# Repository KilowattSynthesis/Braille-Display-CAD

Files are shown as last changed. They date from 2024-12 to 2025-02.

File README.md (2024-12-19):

# Braille-Display-CAD

Experimental design for a braille display using build123d CAD in Python

## Interesting Parts

* 4mm x 8mm DC Motors: https://www.aliexpress.com/item/1005004370822475.html
* 2.8mm x 3.9mm DC Motors: https://www.aliexpress.com/item/1005006897190118.html

## Explored Ideas

### Pogo Spools

* Laser printer fuser-like roller mask.
    * Branch: `archive/pogo-spools`
    * Files: `ideas_pogo_spool_mask/`
* Made PCB with small stepper motors, tiny CAD parts (spools).

### RF Inductors as Electromagnets

* Use Mouser's "RF Inductors" selection, mounting an inductor vertically.
    * Branches: `archive/inductor-smd-vertical`, `archive/inductor-smd-flat`
    * Eaton makes good-looking ones. 3225 metric (1210 imp) is too big; 2520 metric (1008 imp) might be okay. 2012 metric (0805 imp) is great!
    * "Power Inductors - Leaded" are never small enough.
    * Filter to >= 20uH inductance. Filter to >=70 mA.
    * Examples (Vertical-Mount):
        * BWLD00241715 -> Not stocked in smaller quantities, though.
            * 2.4 mm x 1.72 mm x 1.52 mm
        * LBR2012T470M -> 0805 imp (2012 metric). 47uH. 75mA rated max.
    * Examples (Horizontal-Mount):
        * VLS201612CX-220M-1 -> 22uF, very good, but shielded.

* Test results:
    * 4mm x 4mm x 3mm 33uH coil-wound SMD power inductor (ASPI-4030S-330M-T) can point a magnet. Magnets stick to the inductor always though.
    * Several inductors, up to 6mm diameter (and 1-2 MH), with 24V get very hot, but don't levitate a 1mm or 2mm neodymium magnet.
        * Good at pointing pointing the magnet, if it starts far away.
        * Cannot remove the magnet from the inductor once it's stuck.

* **Conclusion**: RF inductors don't have enough magnetic force to levitate 1mm or 2mm neodymium magnets.

### Nut/Bolt Grid

* Turn a bolt in a threaded hole/nut. Each bolt is a dot. User directly touches the dot.
* Movement can be done with one motor per dot (very tiny motors, maybe stacked), or motors can be moved between dots (CNC plotter style). Multiple heads can be used.
* Branch: `archive/cnc-plotter`
* Files: `cad/nut_bolt_grid.py`, `cad/vertical_motor_layers.py`

### Silicone Sheet

* Use CNC plotter to manipulate a silicone sheet which can pop up and down.
    * Branch: `archive/silicone-sheet`
    * Files: `cad/silicone_sheet_mold/`

## Unexplored/Unrealized Ideas

* Investigate bi-metallic strip with actuator.
* Investigate shape memory alloy (SMA) approach. Benefit: Would be very quiet.
* Should buy some 4mm solenoids.

* Key and lock mechanism pushes up on the pins

* Use GT2 belt (or similar) to press up on pins.
    * T2.5 belt is probably best - https://www.aliexpress.com/item/1005004668423141.html
    * Could try to TPU 3D print belt with the perfect braille pattern, in a closed loop. Teeth on the inside, and pattern on the outside.
    * Spring pushing on pogo pin flange, on solenoid-relieved cell frame.

* Use CNC plotter to turn pins/bolts for placement. Use hex drive, plus solenoid to mate/un-mate. Build the plotter on a PCB with 3mm linear rails, belts, etc.
    * Branch: `cnc-plotter`
    * Bolt options - Search "M2.5 plunger"
    * Best option: M1.6 Grub Screw, probably.
    * Create top plate with Z-stacked nuts on it.
    * Screw driver or nut will move up and down and turn screws.
    * Search "Micro Linear Motor" for gantry.
    * Focus on M1.6 and M2.5 designs.
    * To move the screw:
        * Use a spring to push the bit up, and a solenoid to pull it down.
        * Use a hex bit maybe, or use rubber friction.
    * BOM:
        * LM3UU linear bearings (ID=3mm, OD=7mm, L=10mm)
        * 3mm Rod x 100mm
        * PM15S Stepper Motors: https://www.aliexpress.com/item/1005005152436475.html
        * GT2 belt
        * GT2 pulley, custom to mate with stepper motor's gear.

* Motors mounted on orthogonal PCBs, with rotating slanted plate to push on the pins.
    * Use magnets as the mating, somehow.

* Microfluidics as valves.

* MEMS on-chip stepper motor:
    * https://www.youtube.com/watch?v=n3YMjgbhvTA
    * Could be useful to drive the screws on the CNC Plotter style.

* Double screw with balls and weird geometry.

* Cams on 2.4mm diameter rods that run along each column of dots.
    * Each cam would have 8 positions, so 45 degrees per position.
    * Would probably need to move table up-and-down independently of the cams.
    * One motor per cam, probably.

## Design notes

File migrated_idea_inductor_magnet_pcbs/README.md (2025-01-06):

This idea (`idea_inductor_magnet_pcbs`) has been moved to this repo: https://github.com/KilowattSynthesis/Braille-Display-Inductors-CAD

Rev 1 PCBs are present here. Rev 2 (another attempt at tiny inductors), and Rev 3 (using 2x big inductors per cell) are in the linked repo.

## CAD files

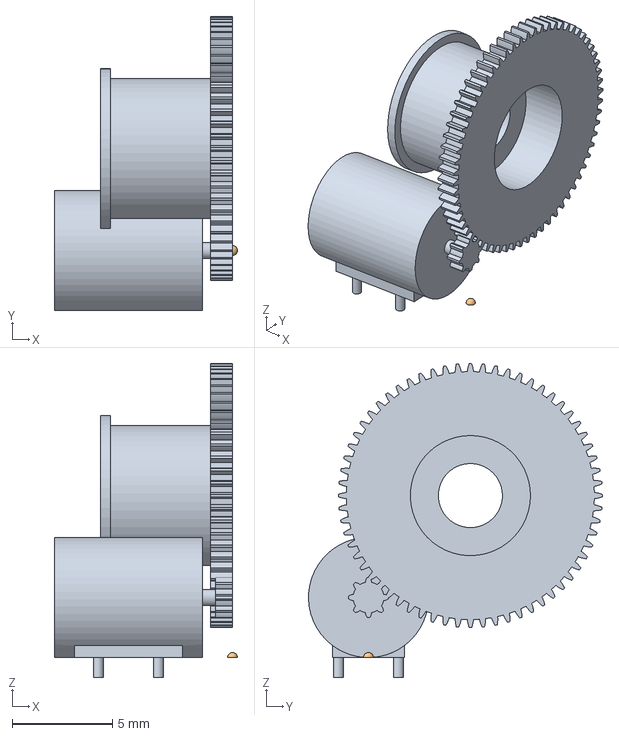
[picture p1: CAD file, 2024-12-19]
idea_pogo_spool_mask/pcb/Braille-Pogo-Frame/lib-cad/spool_motor_assembly.step
9.15 x 14.7 x 15.7 mm

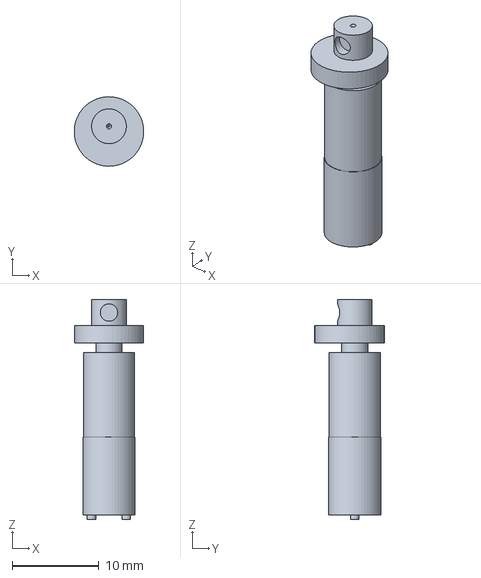
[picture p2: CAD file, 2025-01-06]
migrated_idea_column_rods/Braille-Column-Rods-PCB/lib-cad/assembly_cam_and_dc_motor.step
7.99 x 8.00 x 25.3 mm

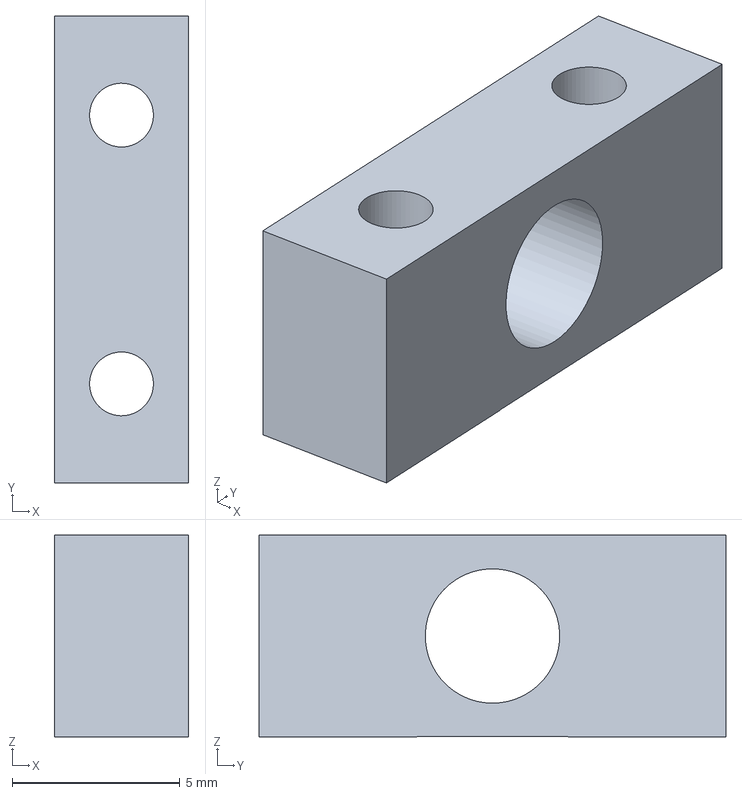
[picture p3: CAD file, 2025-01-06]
migrated_idea_column_rods/Braille-Column-Rods-PCB/lib-cad/bushing_block.step
4.00 x 13.9 x 6.00 mm

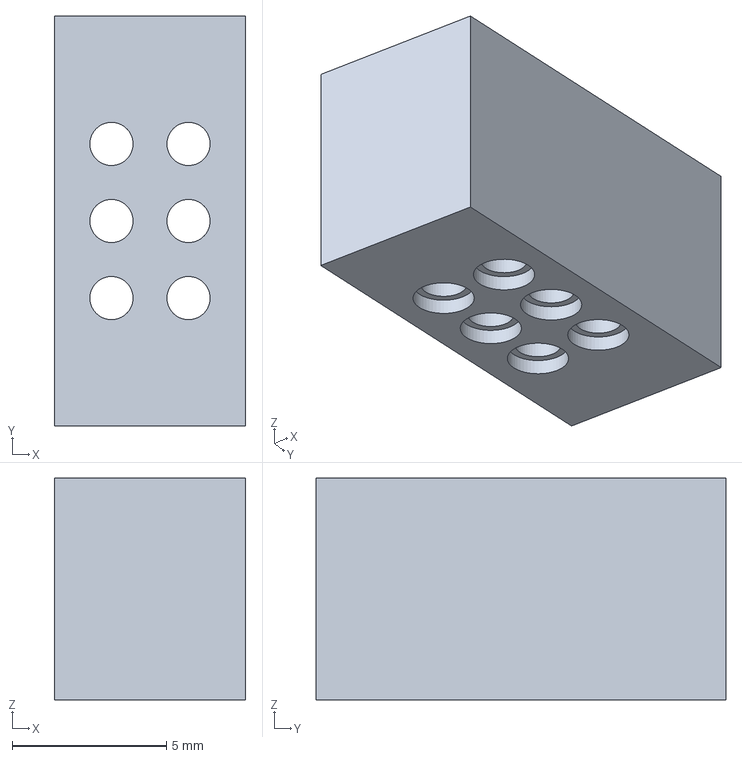
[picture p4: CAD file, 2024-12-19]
idea_pogo_spool_mask/pcb/Braille-Pogo-Frame/lib-cad/housing.step
6.20 x 13.3 x 7.20 mm

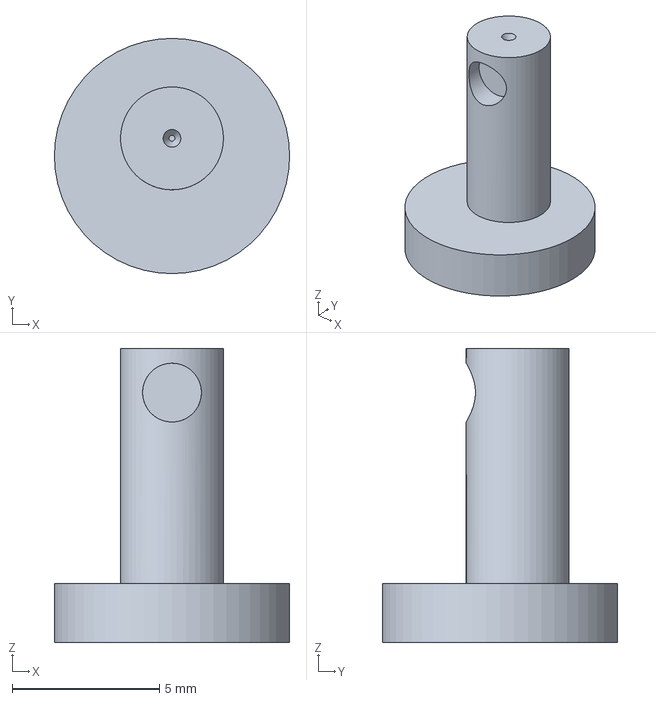
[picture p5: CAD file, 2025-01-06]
migrated_idea_column_rods/Braille-Column-Rods-PCB/lib-cad/cam.step
8.00 x 8.00 x 10.0 mm

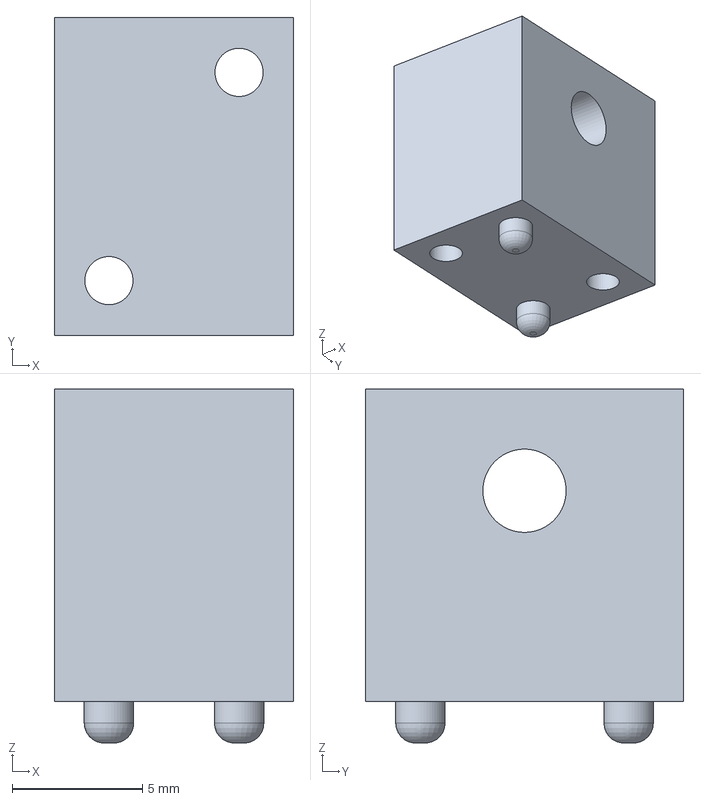
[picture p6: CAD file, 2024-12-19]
idea_pogo_spool_mask/pcb/Braille-Pogo-Frame/lib-cad/horizontal_bar_holder.step
9.20 x 12.2 x 13.6 mm

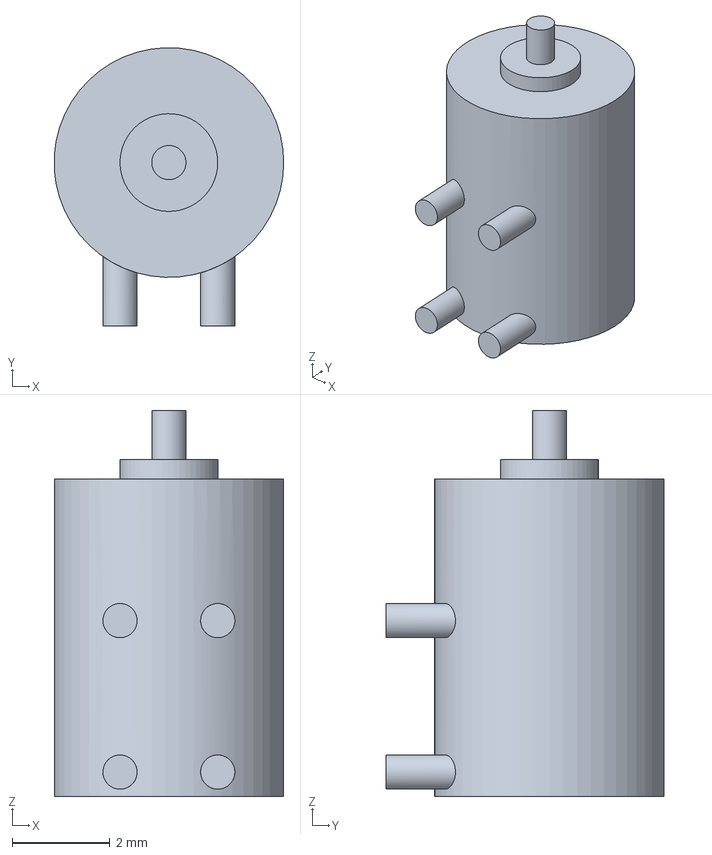
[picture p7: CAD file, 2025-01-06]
migrated_idea_column_rods/Braille-Column-Rods-PCB/lib-cad/micro_stepper_motor_od_4p7.step
4.70 x 5.70 x 7.90 mm

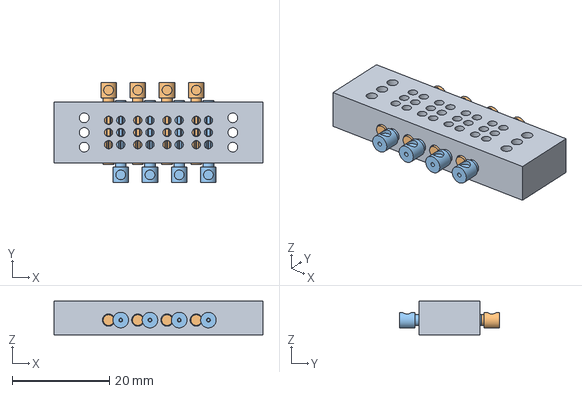
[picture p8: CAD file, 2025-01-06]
migrated_idea_column_rods/Braille-Column-Rods-PCB/lib-cad/octagon_cam_housing_print_in_place.step
42.9 x 20.6 x 6.95 mm

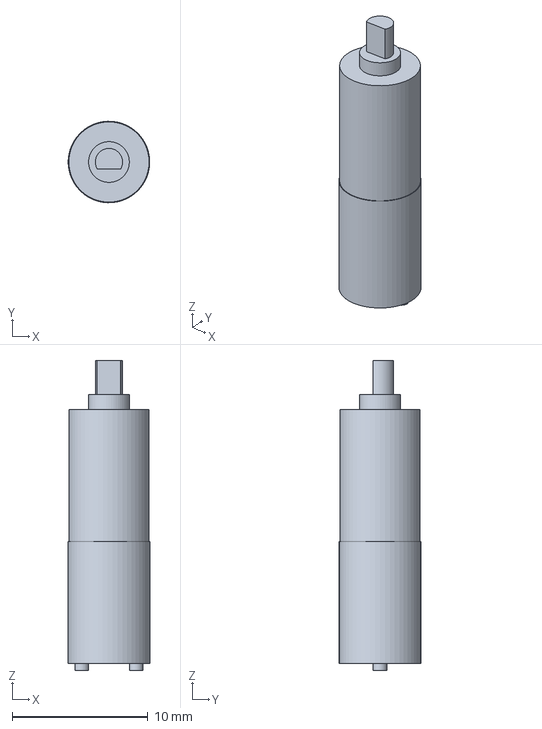
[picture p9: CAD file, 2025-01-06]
migrated_idea_column_rods/Braille-Column-Rods-PCB/lib-cad/dc_motor_and_gearbox_6mm_3_stages.step
5.99 x 6.00 x 22.8 mm

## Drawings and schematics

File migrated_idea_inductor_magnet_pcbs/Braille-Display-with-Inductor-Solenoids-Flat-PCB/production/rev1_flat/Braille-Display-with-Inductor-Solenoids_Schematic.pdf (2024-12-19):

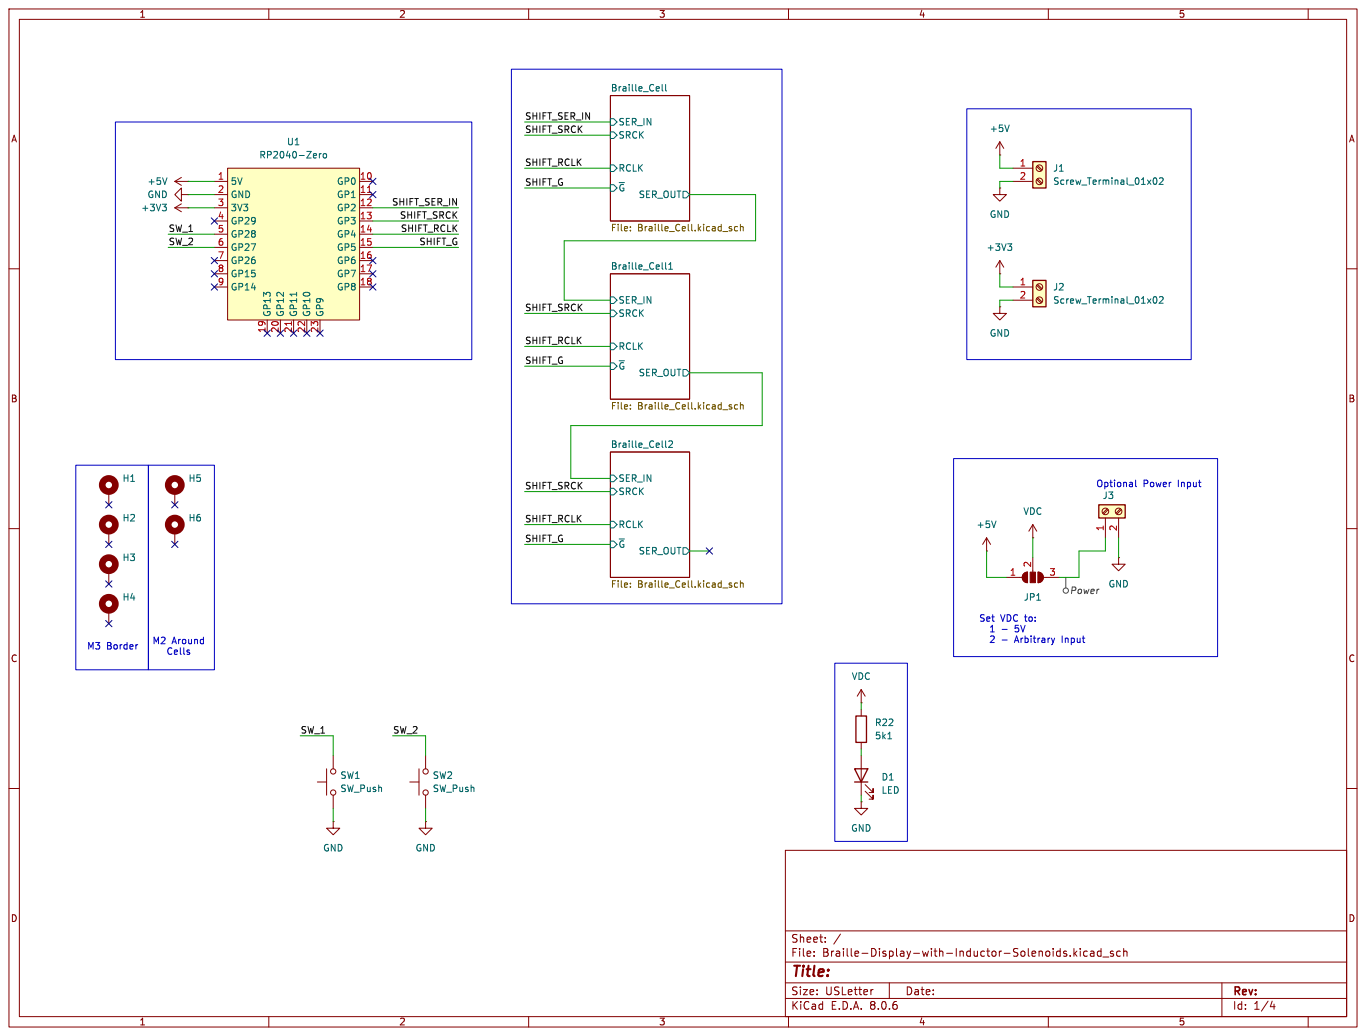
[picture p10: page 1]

SER_IN
Id: 1/4 Title: File: Braille-Display-with-Inductor-Solenoids.kicad_sch Sheet: / SER_OUT SRCK

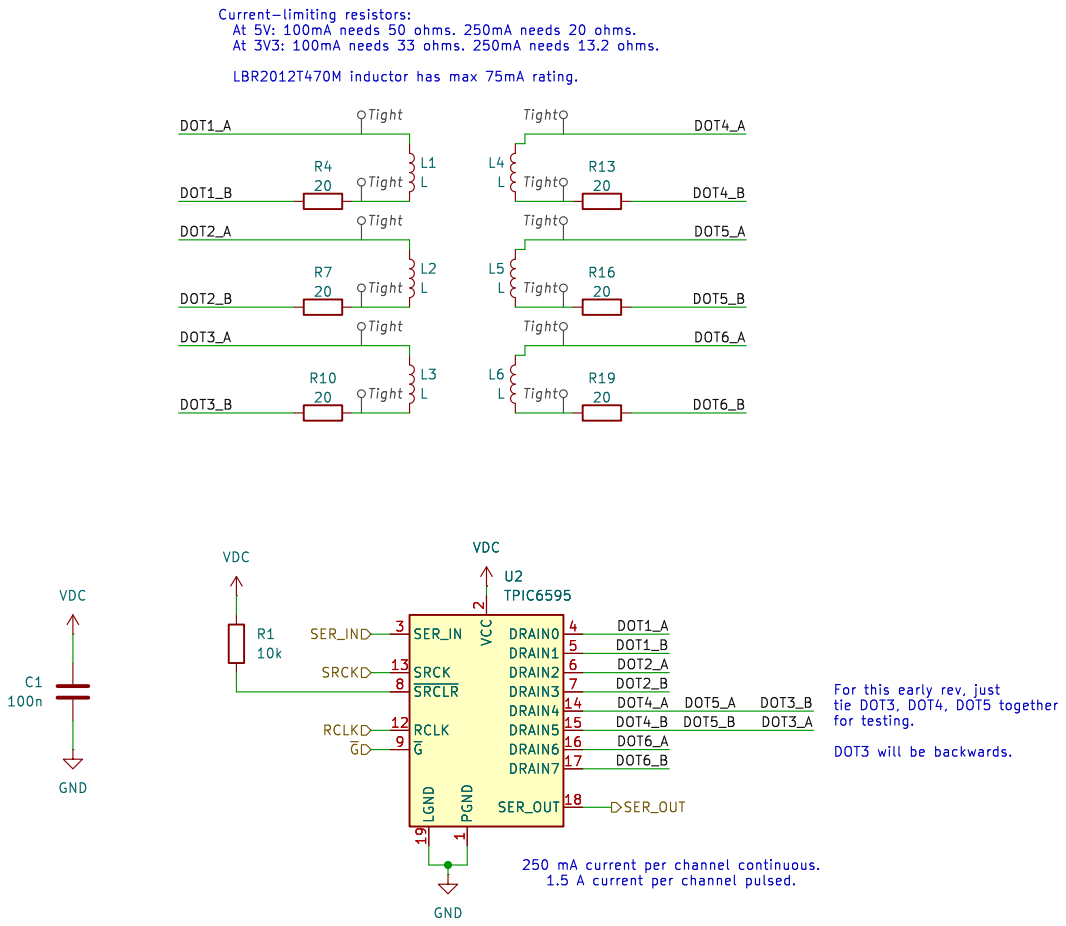
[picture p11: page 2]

1 RCLK 12 SRCK 13 DRAIN4 14 DRAIN5 15 DRAIN6 16 DRAIN7 17 SER_OUT 18 LGND 19 VCC

For this early rev, just
tie DOT3, DOT4, DOT5 together

for testing. DOT3 will be backwards. 250 mA current per channel continuous. 1.5 A current per channel pulsed.

Id: 2/4 Title: File: Braille_Cell.kicad_sch Sheet: /Braille_Cell/

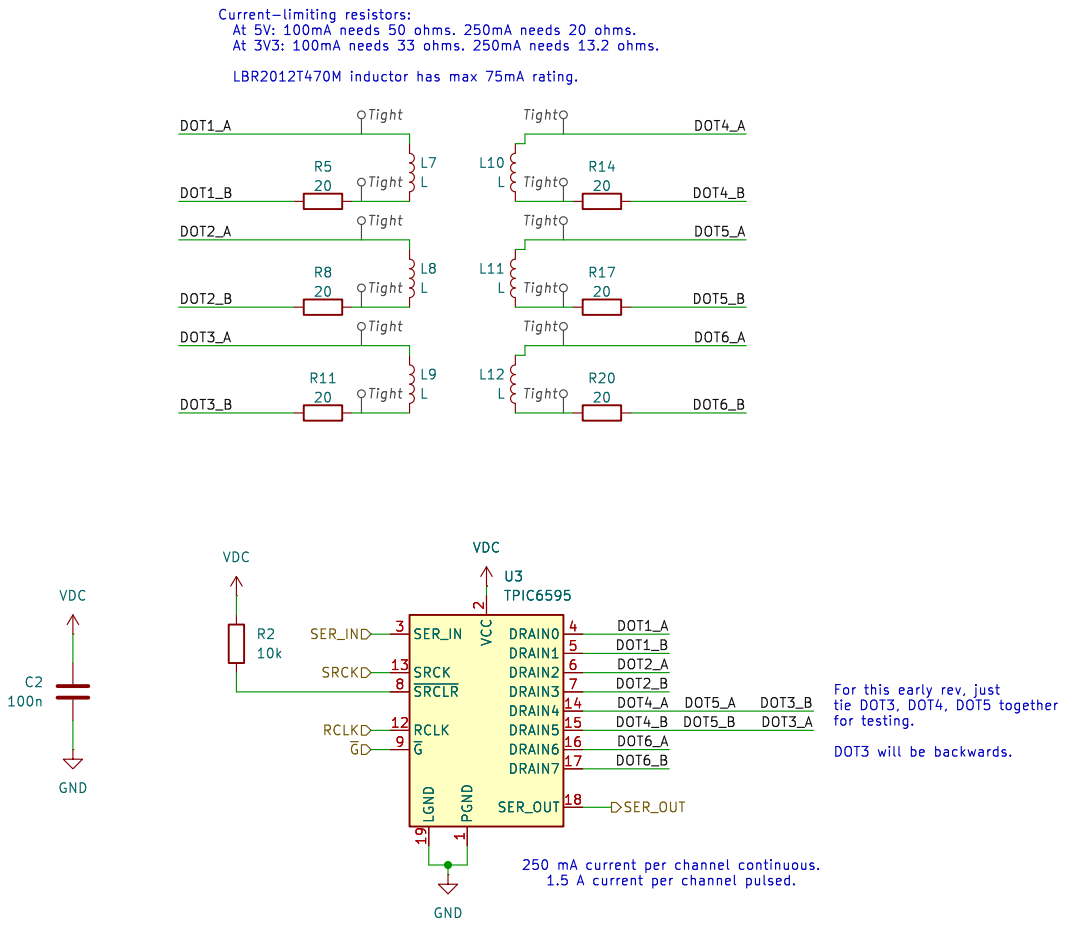
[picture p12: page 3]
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

tie DOT3, DOT4, DOT5 together
for testing. DOT3 will be backwards.

Id: 3/4 Title: File: Braille_Cell.kicad_sch Sheet: /Braille_Cell1/

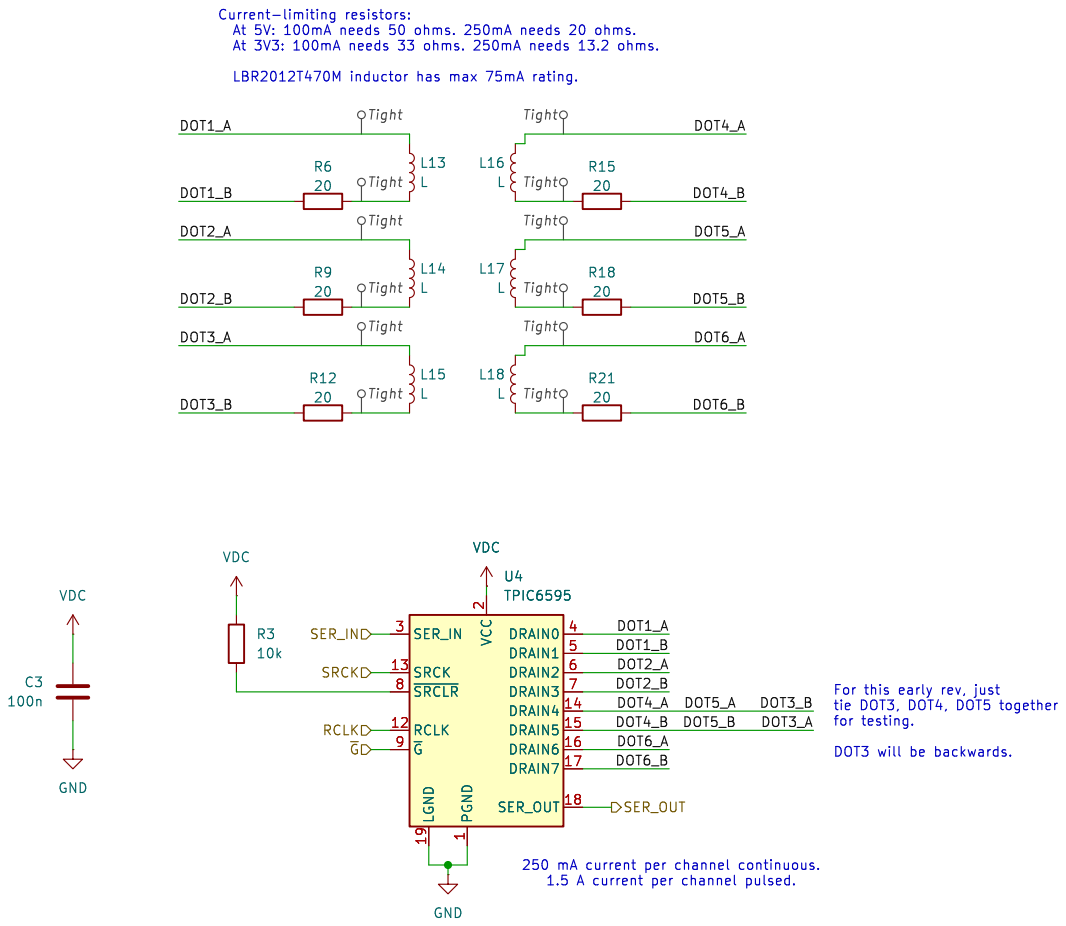
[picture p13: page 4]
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

tie DOT3, DOT4, DOT5 together
for testing. DOT3 will be backwards.

Id: 4/4 Title: File: Braille_Cell.kicad_sch Sheet: /Braille_Cell2/

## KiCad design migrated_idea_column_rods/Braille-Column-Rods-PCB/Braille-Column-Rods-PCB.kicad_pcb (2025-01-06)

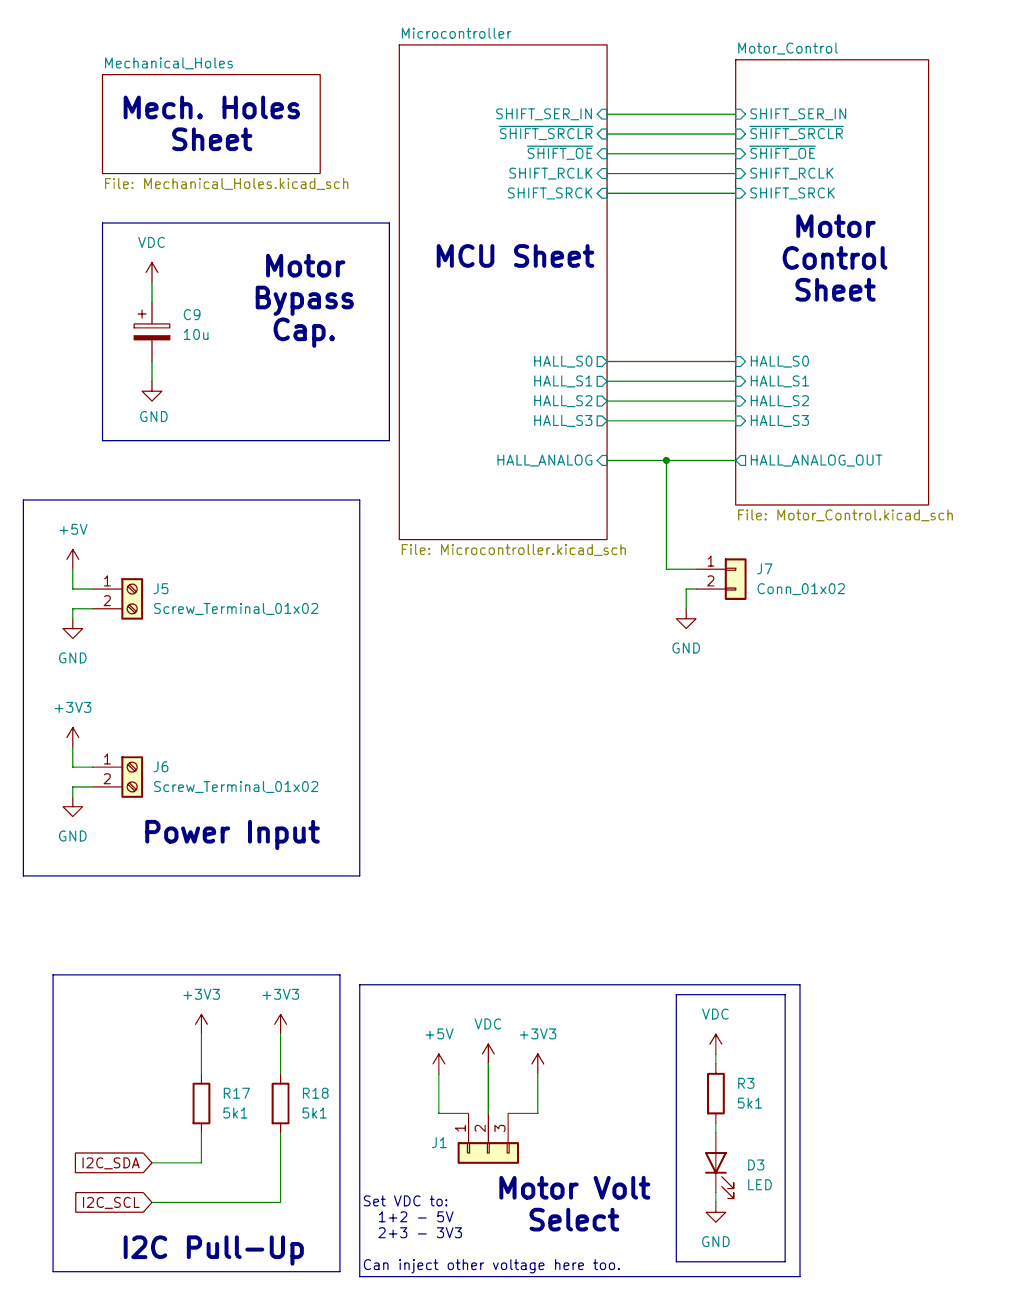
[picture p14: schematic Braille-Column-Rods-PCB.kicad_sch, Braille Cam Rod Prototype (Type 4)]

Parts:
C9: 10u; CP_Radial_D6.3mm_P2.50mm
D3: LED; LED_0603_1608Metric_Pad1.05x0.95mm_HandSolder
J1: Conn_01x03; PinHeader_1x03_P2.54mm_Vertical
J5, J6: Screw_Terminal_01x02; TerminalBlock_bornier-2_P5.08mm
J7: Conn_01x02; PinHeader_1x02_P2.54mm_Vertical
R3, R17, R18: 5k1; R_0603_1608Metric_Pad0.98x0.95mm_HandSolder

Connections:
+3V3: J1.3, J6.1, R17.1, R18.1; also elsewhere on the board
+5V: J1.1, J5.1; also elsewhere on the board
/Microcontroller/HALL_ANALOG: J7.1; also elsewhere on the board
GND: C9.2, D3.1 (K), J5.2, J6.2, J7.2; also elsewhere on the board
I2C_SCL: R18.2; also elsewhere on the board
I2C_SDA: R17.2; also elsewhere on the board
unnamed: D3.2 (A), R3.2
VDC: C9.1, J1.2, R3.1; also elsewhere on the board

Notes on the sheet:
Motor Volt Select
Motor Bypass Cap.
Mech. Holes Sheet
I2C Pull-Up
Set VDC to: 1+2 - 5V 2+3 - 3V3 Can inject other voltage here too.
MCU Sheet
Power Input
Motor Control Sheet

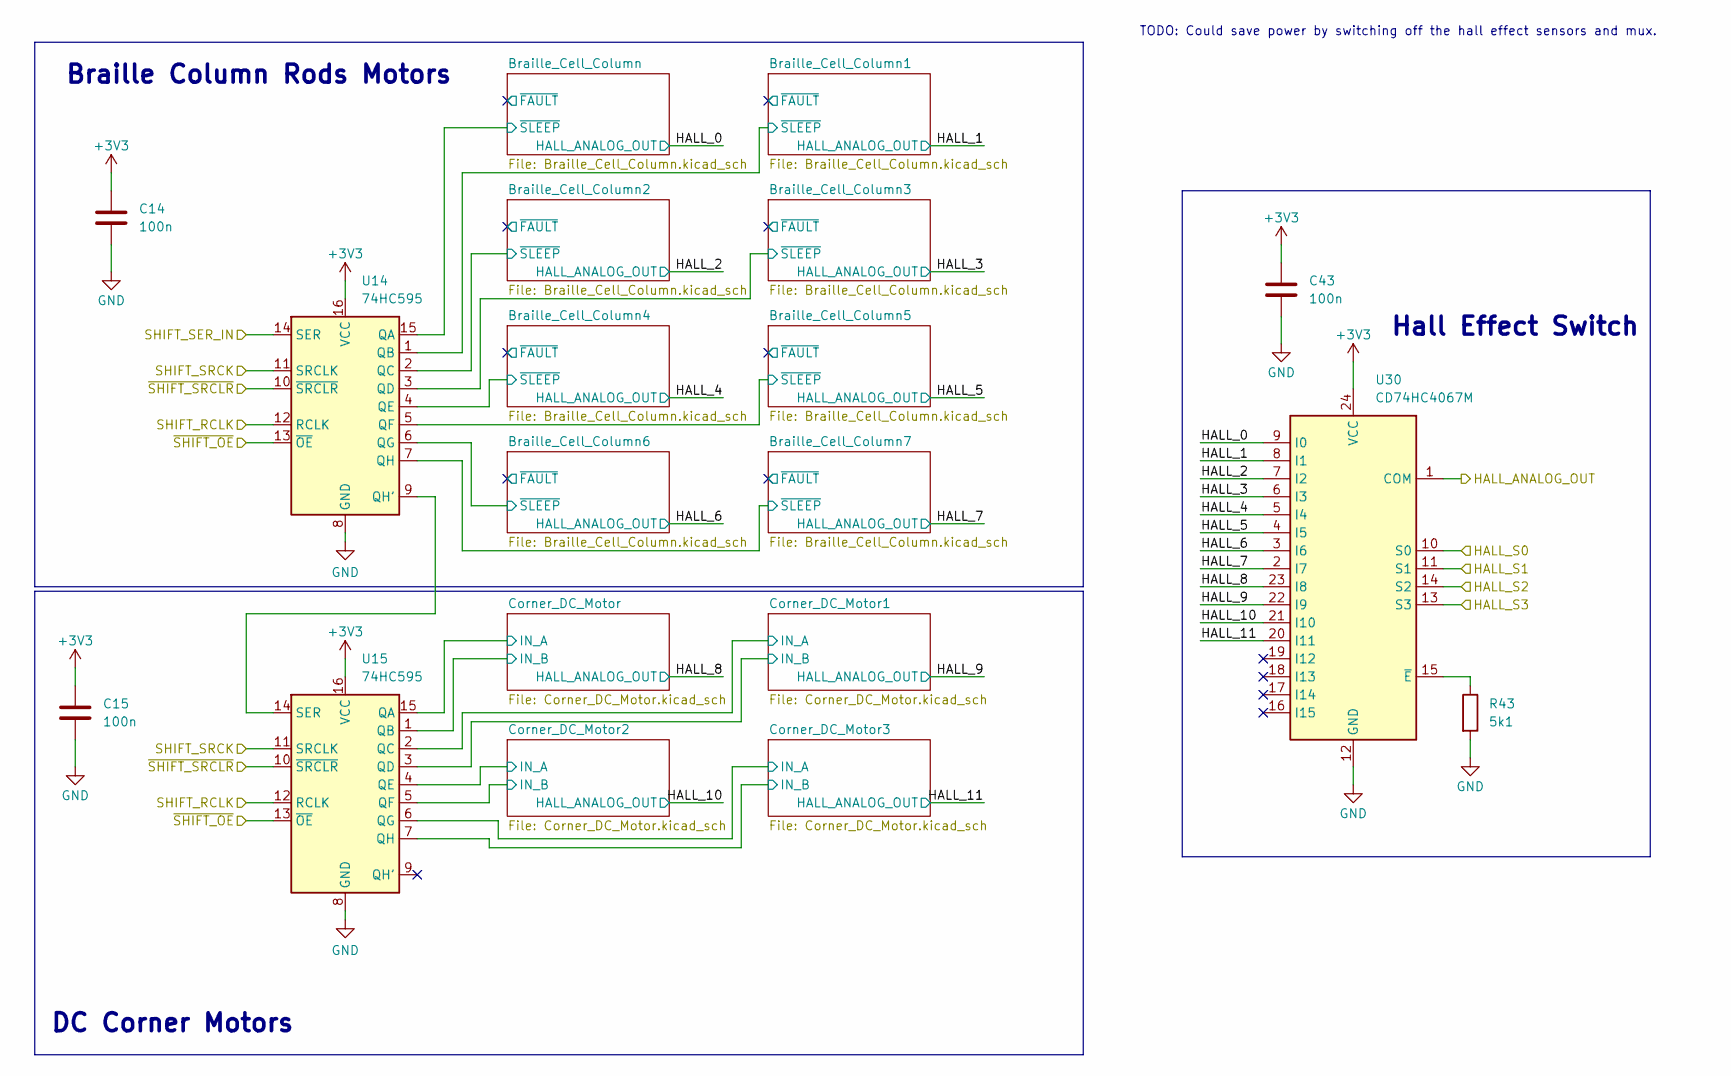
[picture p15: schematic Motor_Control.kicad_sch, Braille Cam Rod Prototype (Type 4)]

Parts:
C14, C15, C43: 100n; C_0603_1608Metric_Pad1.08x0.95mm_HandSolder
R43: 5k1; R_0603_1608Metric_Pad0.98x0.95mm_HandSolder
U14, U15: 74HC595; SOP-16_3.9x9.9mm_P1.27mm
U30: CD74HC4067M; SOIC-24W_7.5x15.4mm_P1.27mm

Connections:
+3V3: C14.1, C15.1, C43.1, U14.16 (VCC), U15.16 (VCC), U30.24 (VCC); also elsewhere on the board
/Microcontroller/HALL_ANALOG: U30.1 (COM); also elsewhere on the board
/Microcontroller/HALL_S0: U30.10 (S0); also elsewhere on the board
/Microcontroller/HALL_S1: U30.11 (S1); also elsewhere on the board
/Microcontroller/HALL_S2: U30.14 (S2); also elsewhere on the board
/Microcontroller/HALL_S3: U30.13 (S3); also elsewhere on the board
/Microcontroller/SHIFT_RCLK: U14.12 (RCLK), U15.12 (RCLK); also elsewhere on the board
/Microcontroller/SHIFT_SER_IN: U14.14 (SER); also elsewhere on the board
/Microcontroller/SHIFT_SRCK: U14.11 (SRCLK), U15.11 (SRCLK); also elsewhere on the board
/Microcontroller/~SHIFT_OE: U14.13 (~OE), U15.13 (~OE); also elsewhere on the board
/Microcontroller/~SHIFT_SRCLR: U14.10 (~SRCLR), U15.10 (~SRCLR); also elsewhere on the board
/Motor_Control/Braille_Cell_Column1/~SLEEP: U14.1 (QB); also elsewhere on the board
/Motor_Control/Braille_Cell_Column2/~SLEEP: U14.2 (QC); also elsewhere on the board
/Motor_Control/Braille_Cell_Column3/~SLEEP: U14.3 (QD); also elsewhere on the board
/Motor_Control/Braille_Cell_Column4/~SLEEP: U14.4 (QE); also elsewhere on the board
/Motor_Control/Braille_Cell_Column5/~SLEEP: U14.5 (QF); also elsewhere on the board
/Motor_Control/Braille_Cell_Column6/~SLEEP: U14.6 (QG); also elsewhere on the board
/Motor_Control/Braille_Cell_Column7/~SLEEP: U14.7 (QH); also elsewhere on the board
/Motor_Control/Braille_Cell_Column/~SLEEP: U14.15 (QA); also elsewhere on the board
/Motor_Control/Corner_DC_Motor1/IN_A: U15.2 (QC); also elsewhere on the board
/Motor_Control/Corner_DC_Motor1/IN_B: U15.3 (QD); also elsewhere on the board
/Motor_Control/Corner_DC_Motor2/IN_A: U15.4 (QE); also elsewhere on the board
/Motor_Control/Corner_DC_Motor2/IN_B: U15.5 (QF); also elsewhere on the board
/Motor_Control/Corner_DC_Motor3/IN_A: U15.6 (QG); also elsewhere on the board
/Motor_Control/Corner_DC_Motor3/IN_B: U15.7 (QH); also elsewhere on the board
/Motor_Control/Corner_DC_Motor/IN_A: U15.15 (QA); also elsewhere on the board
/Motor_Control/Corner_DC_Motor/IN_B: U15.1 (QB); also elsewhere on the board
/Motor_Control/HALL_0: U30.9 (I0); also elsewhere on the board
/Motor_Control/HALL_1: U30.8 (I1); also elsewhere on the board
/Motor_Control/HALL_2: U30.7 (I2); also elsewhere on the board
/Motor_Control/HALL_3: U30.6 (I3); also elsewhere on the board
/Motor_Control/HALL_4: U30.5 (I4); also elsewhere on the board
/Motor_Control/HALL_5: U30.4 (I5); also elsewhere on the board
/Motor_Control/HALL_6: U30.3 (I6); also elsewhere on the board
/Motor_Control/HALL_7: U30.2 (I7); also elsewhere on the board
/Motor_Control/HALL_8: U30.23 (I8); also elsewhere on the board
/Motor_Control/HALL_9: U30.22 (I9); also elsewhere on the board
/Motor_Control/HALL_10: U30.21 (I10); also elsewhere on the board
/Motor_Control/HALL_11: U30.20 (I11); also elsewhere on the board
GND: C14.2, C15.2, C43.2, R43.2, U14.8 (GND), U15.8 (GND), U30.12 (GND); also elsewhere on the board
unnamed: U14.9 (QH'), U15.14 (SER)
unnamed: R43.1, U30.15 (~E)

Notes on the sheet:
Hall Effect Switch
Braille Column Rods Motors
TODO: Could save power by switching off the hall effect sensors and mux.
DC Corner Motors

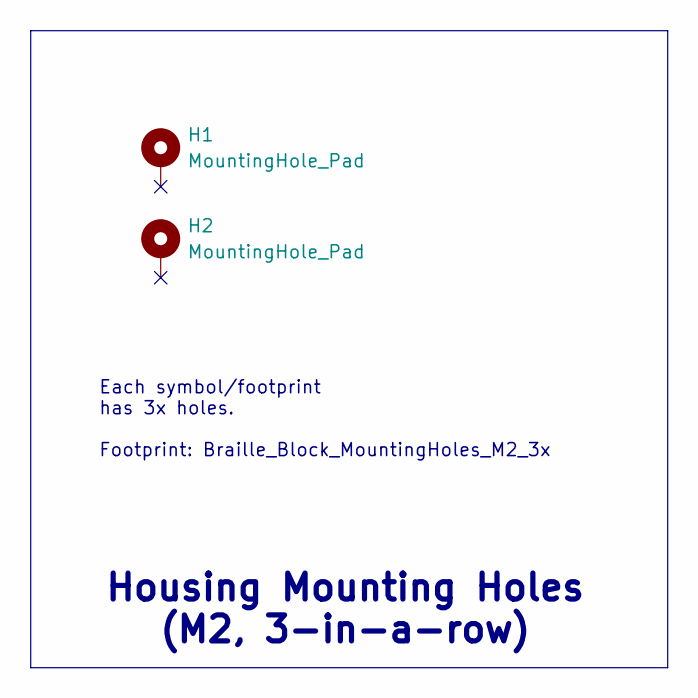
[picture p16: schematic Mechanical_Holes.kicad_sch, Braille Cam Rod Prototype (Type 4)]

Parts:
H1, H2: MountingHole_Pad; Braille_Block_MountingHoles_M2_3x

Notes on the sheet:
Each symbol/footprint has 3x holes. Footprint: Braille_Block_MountingHoles_M2_3x
Housing Mounting Holes (M2, 3-in-a-row)

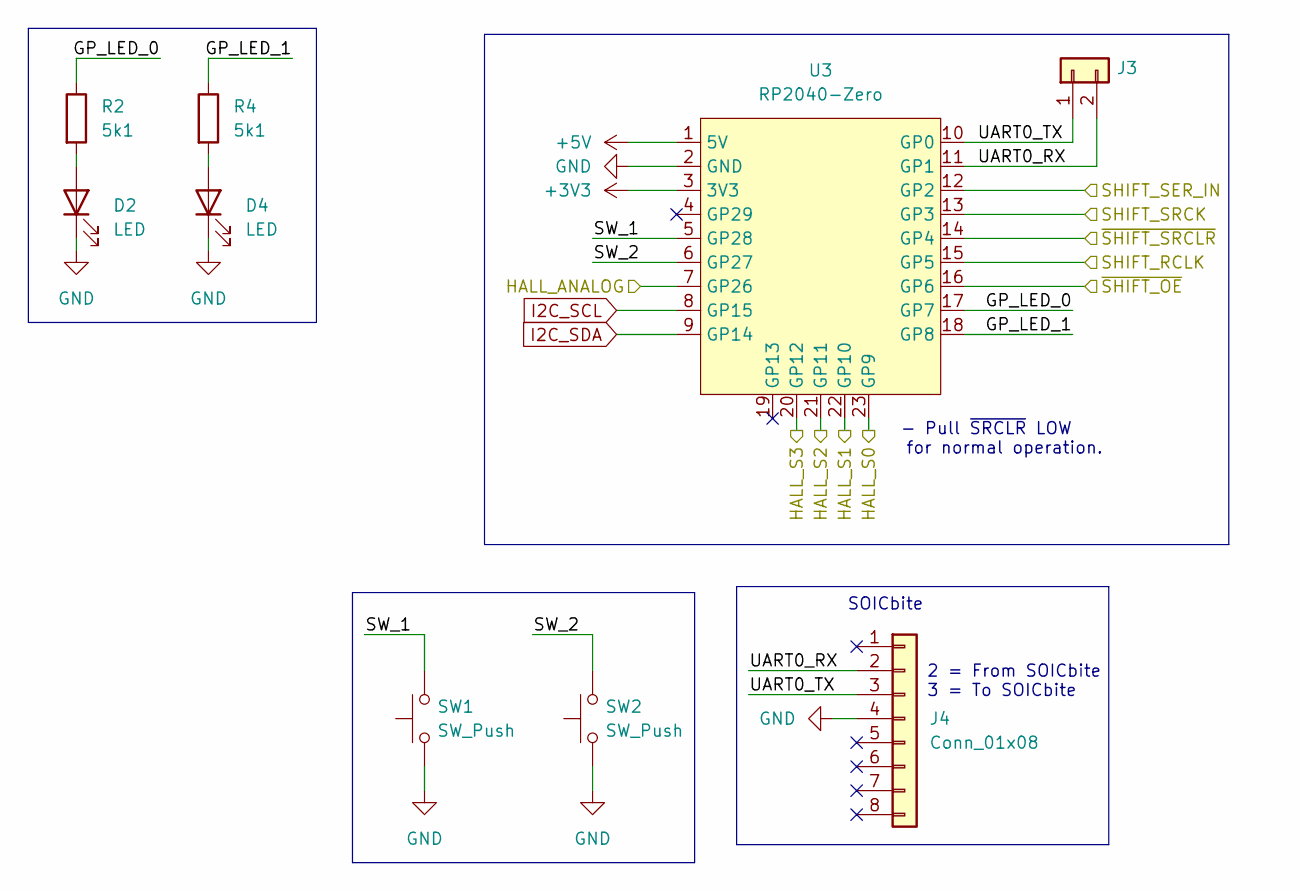
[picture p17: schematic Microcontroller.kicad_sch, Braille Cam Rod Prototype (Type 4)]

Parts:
D2, D4: LED; LED_0603_1608Metric_Pad1.05x0.95mm_HandSolder
J3: Conn_01x02; PinHeader_1x02_P2.54mm_Vertical
J4: Conn_01x08; SOICbite_clipProgSmall
R2, R4: 5k1; R_0603_1608Metric_Pad0.98x0.95mm_HandSolder
SW1, SW2: SW_Push; PushButtonSMD_2.93x3.9
U3: RP2040-Zero; RP2040 Zero

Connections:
+3V3: U3.3 (3V3); also elsewhere on the board
+5V: U3.1 (5V); also elsewhere on the board
/Microcontroller/GP_LED_0: R2.1, U3.17 (GP7)
/Microcontroller/GP_LED_1: R4.1, U3.18 (GP8)
/Microcontroller/HALL_ANALOG: U3.7 (GP26); also elsewhere on the board
/Microcontroller/HALL_S0: U3.23 (GP9); also elsewhere on the board
/Microcontroller/HALL_S1: U3.22 (GP10); also elsewhere on the board
/Microcontroller/HALL_S2: U3.21 (GP11); also elsewhere on the board
/Microcontroller/HALL_S3: U3.20 (GP12); also elsewhere on the board
/Microcontroller/SHIFT_RCLK: U3.15 (GP5); also elsewhere on the board
/Microcontroller/SHIFT_SER_IN: U3.12 (GP2); also elsewhere on the board
/Microcontroller/SHIFT_SRCK: U3.13 (GP3); also elsewhere on the board
/Microcontroller/SW_1: SW1.2, U3.5 (GP28)
/Microcontroller/SW_2: SW2.2, U3.6 (GP27)
/Microcontroller/UART0_RX: J3.2, J4.2, U3.11 (GP1)
/Microcontroller/UART0_TX: J3.1, J4.3, U3.10 (GP0)
/Microcontroller/~SHIFT_OE: U3.16 (GP6); also elsewhere on the board
/Microcontroller/~SHIFT_SRCLR: U3.14 (GP4); also elsewhere on the board
GND: D2.1 (K), D4.1 (K), J4.4, SW1.1, SW2.1, U3.2 (GND); also elsewhere on the board
I2C_SCL: U3.8 (GP15); also elsewhere on the board
I2C_SDA: U3.9 (GP14); also elsewhere on the board
unnamed: D2.2 (A), R2.2
unnamed: D4.2 (A), R4.2

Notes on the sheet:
SOICbite
2 = From SOICbite 3 = To SOICbite
- Pull ~{SRCLR} LOW for normal operation.

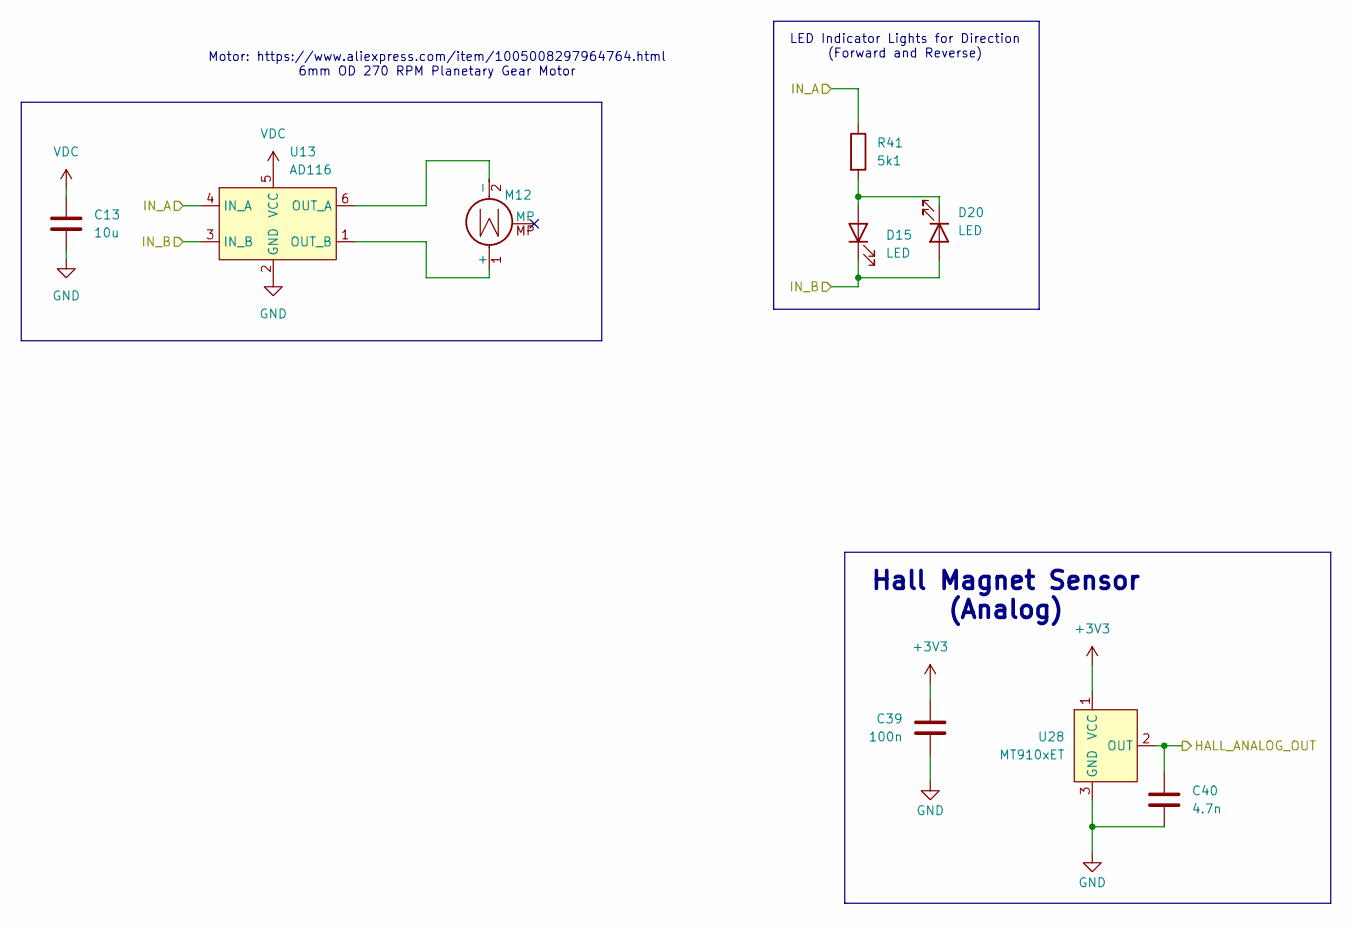
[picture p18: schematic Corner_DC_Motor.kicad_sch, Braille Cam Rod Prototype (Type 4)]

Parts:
C13: 10u; C_1206_3216Metric_Pad1.33x1.80mm_HandSolder
C39: 100n; C_0603_1608Metric_Pad1.08x0.95mm_HandSolder
C40: 4.7n; C_0603_1608Metric_Pad1.08x0.95mm_HandSolder
D15, D20: LED; LED_0603_1608Metric_Pad1.05x0.95mm_HandSolder
M12: Motor_DC_With_MP; DC_Motor_6mm_OD_with_3_Stage_Gearbox
R41: 5k1; R_0603_1608Metric_Pad0.98x0.95mm_HandSolder
U13: AD116; SOT-23-6
U28: MT910xET; SOT-23-Hall

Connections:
+3V3: C39.1, U28.1 (VCC); also elsewhere on the board
/Motor_Control/Corner_DC_Motor3/IN_A: R41.1, U13.4 (IN_A); also elsewhere on the board
/Motor_Control/Corner_DC_Motor3/IN_B: D15.1 (K), D20.2 (A), U13.3 (IN_B); also elsewhere on the board
/Motor_Control/HALL_11: C40.1, U28.2 (OUT); also elsewhere on the board
GND: C13.2, C39.2, C40.2, U13.2 (GND), U28.3 (GND); also elsewhere on the board
unnamed: D15.2 (A), D20.1 (K), R41.2
unnamed: M12.1 (+), U13.1 (OUT_B)
unnamed: M12.2 (-), U13.6 (OUT_A)
VDC: C13.1, U13.5 (VCC); also elsewhere on the board

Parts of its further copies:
C10, C11, C12: 10u; C_1206_3216Metric_Pad1.33x1.80mm_HandSolder
C33, C35, C37: 100n; C_0603_1608Metric_Pad1.08x0.95mm_HandSolder
C34, C36, C38: 4.7n; C_0603_1608Metric_Pad1.08x0.95mm_HandSolder
D12, D13, D14, D17, D18, D19: LED; LED_0603_1608Metric_Pad1.05x0.95mm_HandSolder
M9, M10, M11: Motor_DC_With_MP; DC_Motor_6mm_OD_with_3_Stage_Gearbox
R38, R39, R40: 5k1; R_0603_1608Metric_Pad0.98x0.95mm_HandSolder
U10, U11, U12: AD116; SOT-23-6
U25, U26, U27: MT910xET; SOT-23-Hall

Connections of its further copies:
+3V3: C33.1, C35.1, C37.1, U25.1 (VCC), U26.1 (VCC), U27.1 (VCC); also elsewhere on the board
/Motor_Control/Corner_DC_Motor1/IN_A: R39.1, U11.4 (IN_A); also elsewhere on the board
/Motor_Control/Corner_DC_Motor1/IN_B: D13.1 (K), D18.2 (A), U11.3 (IN_B); also elsewhere on the board
/Motor_Control/Corner_DC_Motor2/IN_A: R40.1, U12.4 (IN_A); also elsewhere on the board
/Motor_Control/Corner_DC_Motor2/IN_B: D14.1 (K), D19.2 (A), U12.3 (IN_B); also elsewhere on the board
/Motor_Control/Corner_DC_Motor/IN_A: R38.1, U10.4 (IN_A); also elsewhere on the board
/Motor_Control/Corner_DC_Motor/IN_B: D12.1 (K), D17.2 (A), U10.3 (IN_B); also elsewhere on the board
/Motor_Control/HALL_8: C34.1, U25.2 (OUT); also elsewhere on the board
/Motor_Control/HALL_9: C36.1, U26.2 (OUT); also elsewhere on the board
/Motor_Control/HALL_10: C38.1, U27.2 (OUT); also elsewhere on the board
GND: C10.2, C11.2, C12.2, C33.2, C34.2, C35.2, C36.2, C37.2, C38.2, U10.2 (GND), U11.2 (GND), U12.2 (GND), U25.3 (GND), U26.3 (GND), U27.3 (GND); also elsewhere on the board
unnamed: D12.2 (A), D17.1 (K), R38.2
unnamed: D13.2 (A), D18.1 (K), R39.2
unnamed: D14.2 (A), D19.1 (K), R40.2
unnamed: M9.1 (+), U10.1 (OUT_B)
unnamed: M9.2 (-), U10.6 (OUT_A)
unnamed: M10.1 (+), U11.1 (OUT_B)
unnamed: M10.2 (-), U11.6 (OUT_A)
unnamed: M11.1 (+), U12.1 (OUT_B)
unnamed: M11.2 (-), U12.6 (OUT_A)
VDC: C10.1, C11.1, C12.1, U10.5 (VCC), U11.5 (VCC), U12.5 (VCC); also elsewhere on the board

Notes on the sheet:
LED Indicator Lights for Direction (Forward and Reverse)
Hall Magnet Sensor (Analog)
Motor: https://www.aliexpress.com/item/1005008297964764.html 6mm OD 270 RPM Planetary Gear Motor

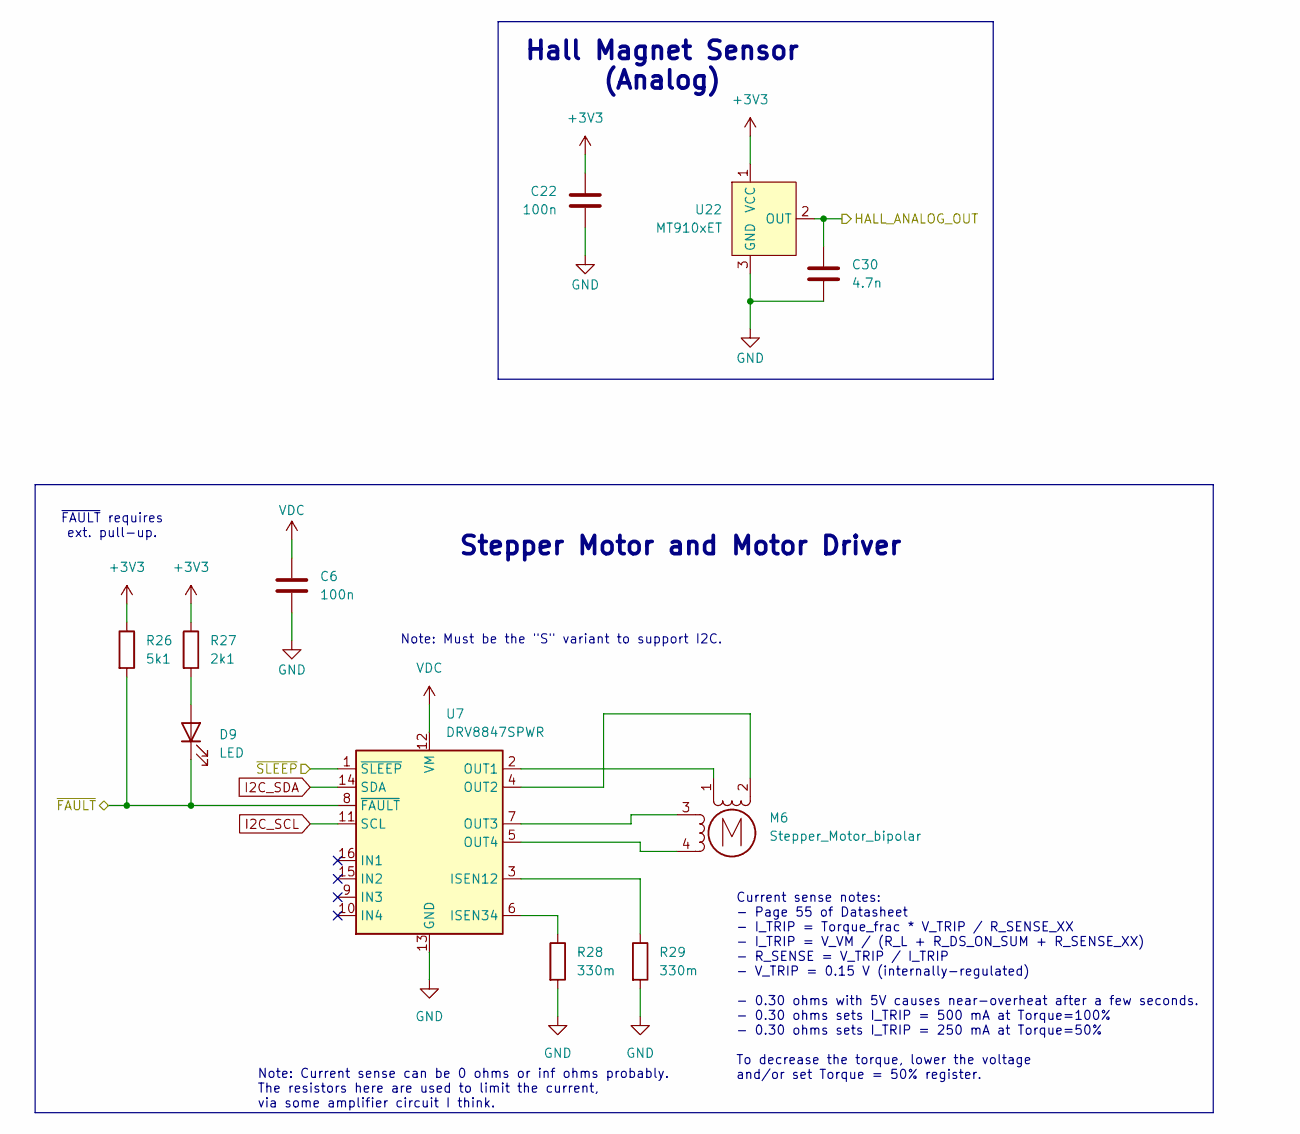
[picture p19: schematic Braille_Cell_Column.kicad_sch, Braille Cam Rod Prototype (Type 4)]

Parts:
C6, C22: 100n; C_0603_1608Metric_Pad1.08x0.95mm_HandSolder
C30: 4.7n; C_0603_1608Metric_Pad1.08x0.95mm_HandSolder
D9: LED; LED_0603_1608Metric_Pad1.05x0.95mm_HandSolder
M6: Stepper_Motor_bipolar; MicroStepper_4.7_OD
R26: 5k1; R_0603_1608Metric_Pad0.98x0.95mm_HandSolder
R27: 2k1; R_0603_1608Metric_Pad0.98x0.95mm_HandSolder
R28, R29: 330m; R_0603_1608Metric_Pad0.98x0.95mm_HandSolder
U7: DRV8847SPWR; TSSOP-16_4.4x5mm_P0.65mm
U22: MT910xET; SOT-23-Hall

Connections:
+3V3: C22.1, R26.1, R27.1, U22.1 (VCC); also elsewhere on the board
/Motor_Control/Braille_Cell_Column5/~FAULT: D9.1 (K), R26.2, U7.8 (~FAULT)
/Motor_Control/Braille_Cell_Column5/~SLEEP: U7.1 (~SLEEP); also elsewhere on the board
/Motor_Control/HALL_5: C30.1, U22.2 (OUT); also elsewhere on the board
GND: C6.2, C22.2, C30.2, R28.2, R29.2, U7.13 (GND), U22.3 (GND); also elsewhere on the board
I2C_SCL: U7.11 (SCL); also elsewhere on the board
I2C_SDA: U7.14 (SDA); also elsewhere on the board
unnamed: D9.2 (A), R27.2
unnamed: M6.2 (-), U7.4 (OUT2)
unnamed: R29.1, U7.3 (ISEN12)
unnamed: R28.1, U7.6 (ISEN34)
unnamed: M6.1, U7.2 (OUT1)
unnamed: M6.3, U7.7 (OUT3)
unnamed: M6.4, U7.5 (OUT4)
VDC: C6.1, U7.12 (VM); also elsewhere on the board

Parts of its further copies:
C1, C2, C3, C4, C5, C7, C8, C17, C18, C19, C20, C21, C23, C24: 100n; C_0603_1608Metric_Pad1.08x0.95mm_HandSolder
C25, C26, C27, C28, C29, C31, C32: 4.7n; C_0603_1608Metric_Pad1.08x0.95mm_HandSolder
D1, D5, D6, D7, D8, D10, D11: LED; LED_0603_1608Metric_Pad1.05x0.95mm_HandSolder
M1, M2, M3, M4, M5, M7, M8: Stepper_Motor_bipolar; MicroStepper_4.7_OD
R1, R8, R12, R16, R22, R30, R34: 5k1; R_0603_1608Metric_Pad0.98x0.95mm_HandSolder
R5, R9, R13, R19, R23, R31, R35: 2k1; R_0603_1608Metric_Pad0.98x0.95mm_HandSolder
R6, R7, R10, R11, R14, R15, R20, R21, R24, R25, R32, R33, R36, R37: 330m; R_0603_1608Metric_Pad0.98x0.95mm_HandSolder
U1, U2, U4, U5, U6, U8, U9: DRV8847SPWR; TSSOP-16_4.4x5mm_P0.65mm
U17, U18, U19, U20, U21, U23, U24: MT910xET; SOT-23-Hall

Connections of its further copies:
+3V3: C17.1, C18.1, C19.1, C20.1, C21.1, C23.1, C24.1, R1.1, R5.1, R8.1, R9.1, R12.1, R13.1, R16.1, R19.1, R22.1, R23.1, R30.1, R31.1, R34.1, R35.1, U17.1 (VCC), U18.1 (VCC), U19.1 (VCC), U20.1 (VCC), U21.1 (VCC), U23.1 (VCC), U24.1 (VCC); also elsewhere on the board
/Motor_Control/Braille_Cell_Column1/~FAULT: D5.1 (K), R8.2, U2.8 (~FAULT)
/Motor_Control/Braille_Cell_Column1/~SLEEP: U2.1 (~SLEEP); also elsewhere on the board
/Motor_Control/Braille_Cell_Column2/~FAULT: D6.1 (K), R12.2, U4.8 (~FAULT)
/Motor_Control/Braille_Cell_Column2/~SLEEP: U4.1 (~SLEEP); also elsewhere on the board
/Motor_Control/Braille_Cell_Column3/~FAULT: D7.1 (K), R16.2, U5.8 (~FAULT)
/Motor_Control/Braille_Cell_Column3/~SLEEP: U5.1 (~SLEEP); also elsewhere on the board
/Motor_Control/Braille_Cell_Column4/~FAULT: D8.1 (K), R22.2, U6.8 (~FAULT)
/Motor_Control/Braille_Cell_Column4/~SLEEP: U6.1 (~SLEEP); also elsewhere on the board
/Motor_Control/Braille_Cell_Column6/~FAULT: D10.1 (K), R30.2, U8.8 (~FAULT)
/Motor_Control/Braille_Cell_Column6/~SLEEP: U8.1 (~SLEEP); also elsewhere on the board
/Motor_Control/Braille_Cell_Column7/~FAULT: D11.1 (K), R34.2, U9.8 (~FAULT)
/Motor_Control/Braille_Cell_Column7/~SLEEP: U9.1 (~SLEEP); also elsewhere on the board
/Motor_Control/Braille_Cell_Column/~FAULT: D1.1 (K), R1.2, U1.8 (~FAULT)
/Motor_Control/Braille_Cell_Column/~SLEEP: U1.1 (~SLEEP); also elsewhere on the board
/Motor_Control/HALL_0: C25.1, U17.2 (OUT); also elsewhere on the board
/Motor_Control/HALL_1: C26.1, U18.2 (OUT); also elsewhere on the board
/Motor_Control/HALL_2: C27.1, U19.2 (OUT); also elsewhere on the board
/Motor_Control/HALL_3: C28.1, U20.2 (OUT); also elsewhere on the board
/Motor_Control/HALL_4: C29.1, U21.2 (OUT); also elsewhere on the board
/Motor_Control/HALL_6: C31.1, U23.2 (OUT); also elsewhere on the board
/Motor_Control/HALL_7: C32.1, U24.2 (OUT); also elsewhere on the board
GND: C1.2, C2.2, C3.2, C4.2, C5.2, C7.2, C8.2, C17.2, C18.2, C19.2, C20.2, C21.2, C23.2, C24.2, C25.2, C26.2, C27.2, C28.2, C29.2, C31.2, C32.2, R6.2, R7.2, R10.2, R11.2, R14.2, R15.2, R20.2, R21.2, R24.2, R25.2, R32.2, R33.2, R36.2, R37.2, U1.13 (GND), U2.13 (GND), U4.13 (GND), U5.13 (GND), U6.13 (GND), U8.13 (GND), U9.13 (GND), U17.3 (GND), U18.3 (GND), U19.3 (GND), U20.3 (GND), U21.3 (GND), U23.3 (GND), U24.3 (GND); also elsewhere on the board
I2C_SCL: U1.11 (SCL), U2.11 (SCL), U4.11 (SCL), U5.11 (SCL), U6.11 (SCL), U8.11 (SCL), U9.11 (SCL); also elsewhere on the board
I2C_SDA: U1.14 (SDA), U2.14 (SDA), U4.14 (SDA), U5.14 (SDA), U6.14 (SDA), U8.14 (SDA), U9.14 (SDA); also elsewhere on the board
unnamed: D1.2 (A), R5.2
unnamed: D5.2 (A), R9.2
unnamed: D6.2 (A), R13.2
unnamed: D7.2 (A), R19.2
unnamed: D8.2 (A), R23.2
unnamed: D10.2 (A), R31.2
unnamed: D11.2 (A), R35.2
unnamed: M1.2 (-), U1.4 (OUT2)
unnamed: M2.2 (-), U2.4 (OUT2)
unnamed: M3.2 (-), U4.4 (OUT2)
unnamed: M4.2 (-), U5.4 (OUT2)
unnamed: M5.2 (-), U6.4 (OUT2)
unnamed: M7.2 (-), U8.4 (OUT2)
unnamed: M8.2 (-), U9.4 (OUT2)
unnamed: R7.1, U1.3 (ISEN12)
unnamed: R6.1, U1.6 (ISEN34)
unnamed: M1.1, U1.2 (OUT1)
unnamed: M1.3, U1.7 (OUT3)
unnamed: M1.4, U1.5 (OUT4)
unnamed: R11.1, U2.3 (ISEN12)
unnamed: R10.1, U2.6 (ISEN34)
unnamed: M2.1, U2.2 (OUT1)
unnamed: M2.3, U2.7 (OUT3)
unnamed: M2.4, U2.5 (OUT4)
unnamed: R15.1, U4.3 (ISEN12)
unnamed: R14.1, U4.6 (ISEN34)
unnamed: M3.1, U4.2 (OUT1)
unnamed: M3.3, U4.7 (OUT3)
unnamed: M3.4, U4.5 (OUT4)
unnamed: R21.1, U5.3 (ISEN12)
unnamed: R20.1, U5.6 (ISEN34)
unnamed: M4.1, U5.2 (OUT1)
unnamed: M4.3, U5.7 (OUT3)
unnamed: M4.4, U5.5 (OUT4)
unnamed: R25.1, U6.3 (ISEN12)
unnamed: R24.1, U6.6 (ISEN34)
unnamed: M5.1, U6.2 (OUT1)
unnamed: M5.3, U6.7 (OUT3)
unnamed: M5.4, U6.5 (OUT4)
unnamed: R33.1, U8.3 (ISEN12)
unnamed: R32.1, U8.6 (ISEN34)
unnamed: M7.1, U8.2 (OUT1)
unnamed: M7.3, U8.7 (OUT3)
unnamed: M7.4, U8.5 (OUT4)
unnamed: R37.1, U9.3 (ISEN12)
unnamed: R36.1, U9.6 (ISEN34)
unnamed: M8.1, U9.2 (OUT1)
unnamed: M8.3, U9.7 (OUT3)
unnamed: M8.4, U9.5 (OUT4)
VDC: C1.1, C2.1, C3.1, C4.1, C5.1, C7.1, C8.1, U1.12 (VM), U2.12 (VM), U4.12 (VM), U5.12 (VM), U6.12 (VM), U8.12 (VM), U9.12 (VM); also elsewhere on the board

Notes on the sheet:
Note: Current sense can be 0 ohms or inf ohms probably. The resistors here are used to limit the current, via some amplifier circuit I think.
Current sense notes: - Page 55 of Datasheet - I_TRIP = Torque_frac * V_TRIP / R_SENSE_XX - I_TRIP = V_VM / (R_L + R_DS_ON_SUM + R_SENSE_XX) - R_SENSE = V_TRIP / I_TRIP - V_TRIP = 0.15 V (internally-regulated) - 0.30 ohms with 5V causes near-overheat after a few seconds. - 0.30 ohms sets I_TRIP = 50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
~{FAULT} requires ext. pull-up.
Note: Must be the "S" variant to support I2C.
Stepper Motor and Motor Driver
Hall Magnet Sensor (Analog)

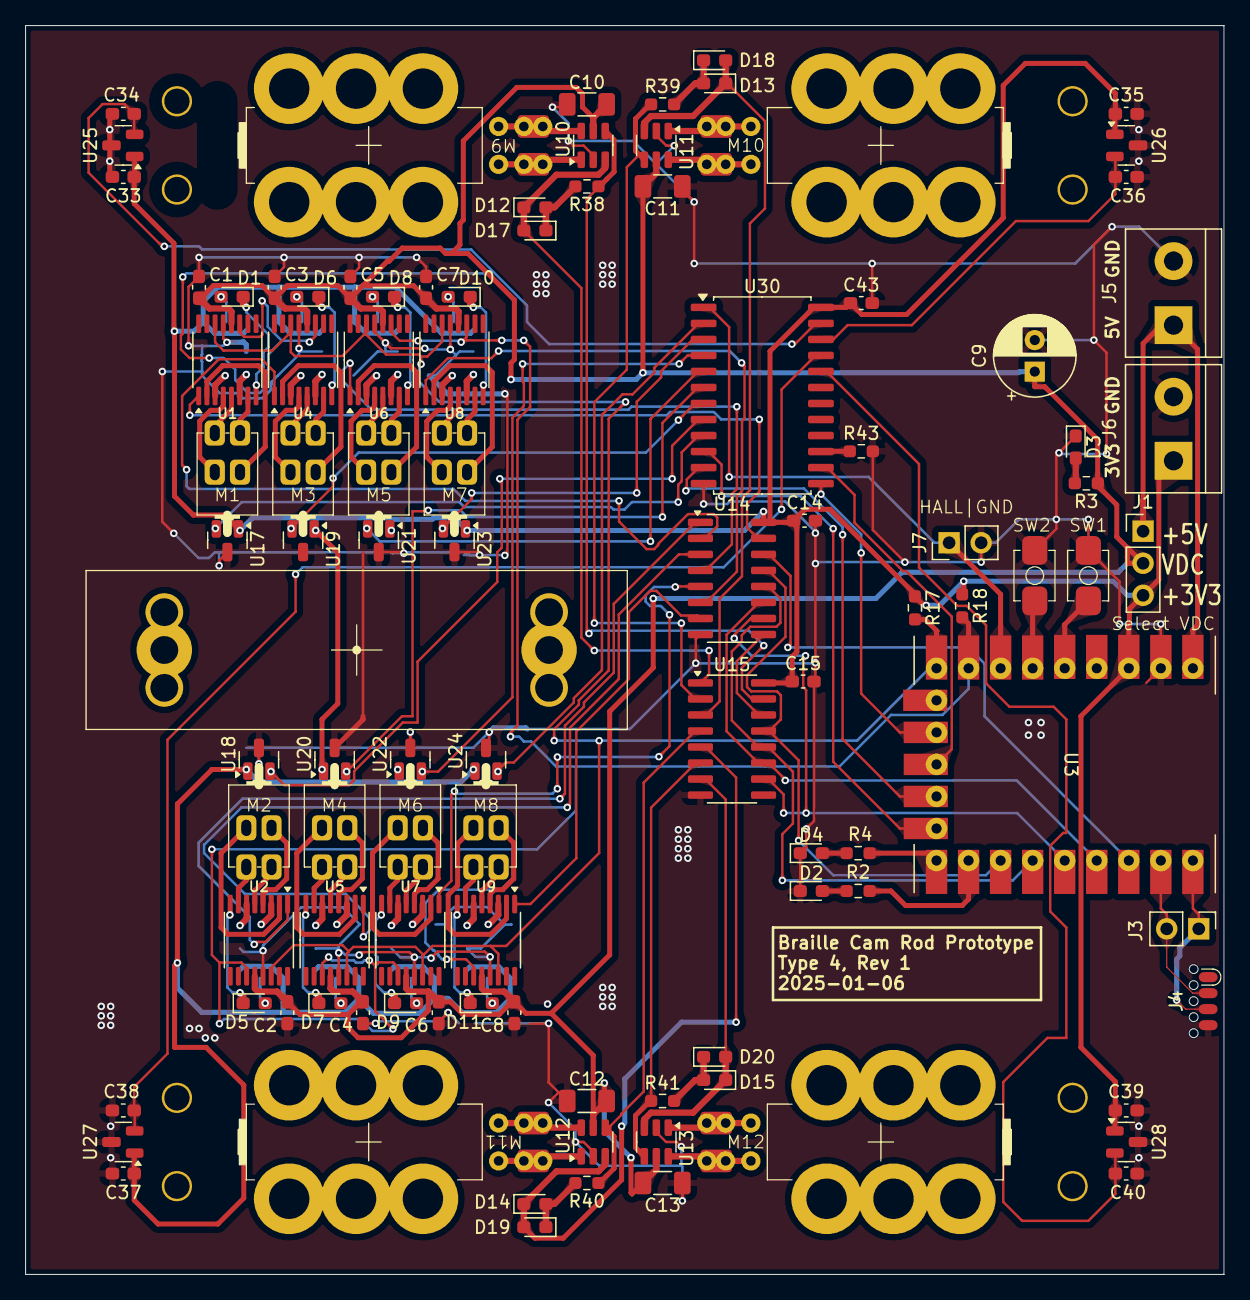
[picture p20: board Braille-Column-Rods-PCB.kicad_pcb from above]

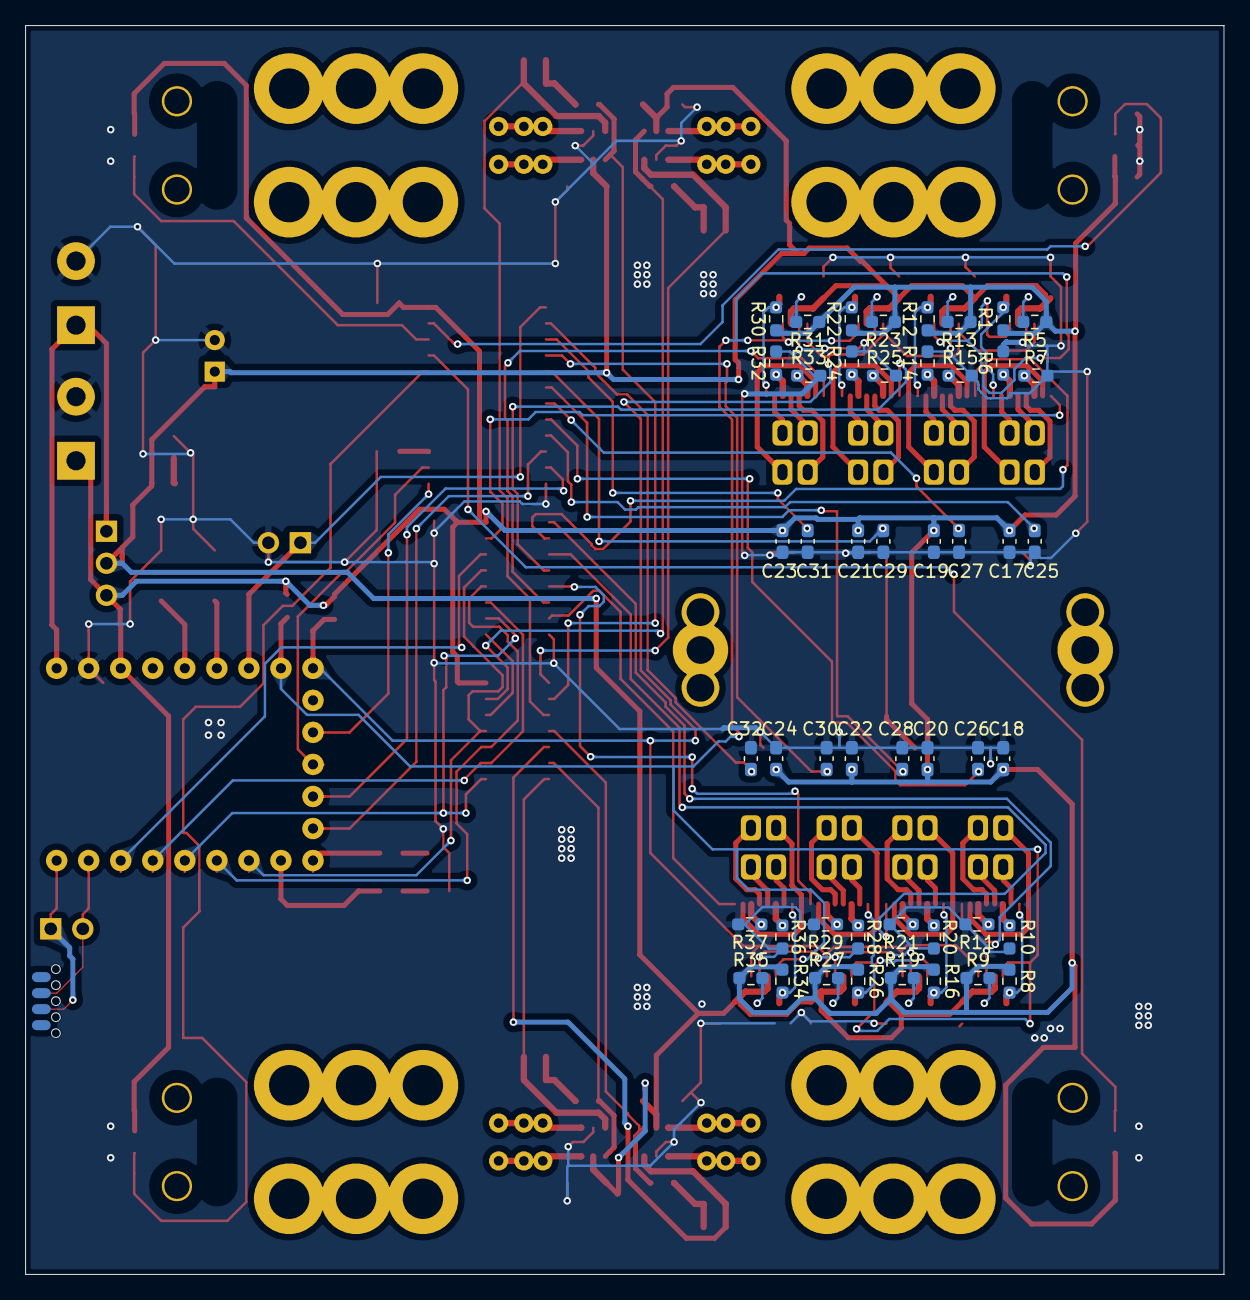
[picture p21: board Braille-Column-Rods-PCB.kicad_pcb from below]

Board: 2 copper layers, 95.0 x 99.0 mm, 151 parts (48 on the bottom side), 131 nets.

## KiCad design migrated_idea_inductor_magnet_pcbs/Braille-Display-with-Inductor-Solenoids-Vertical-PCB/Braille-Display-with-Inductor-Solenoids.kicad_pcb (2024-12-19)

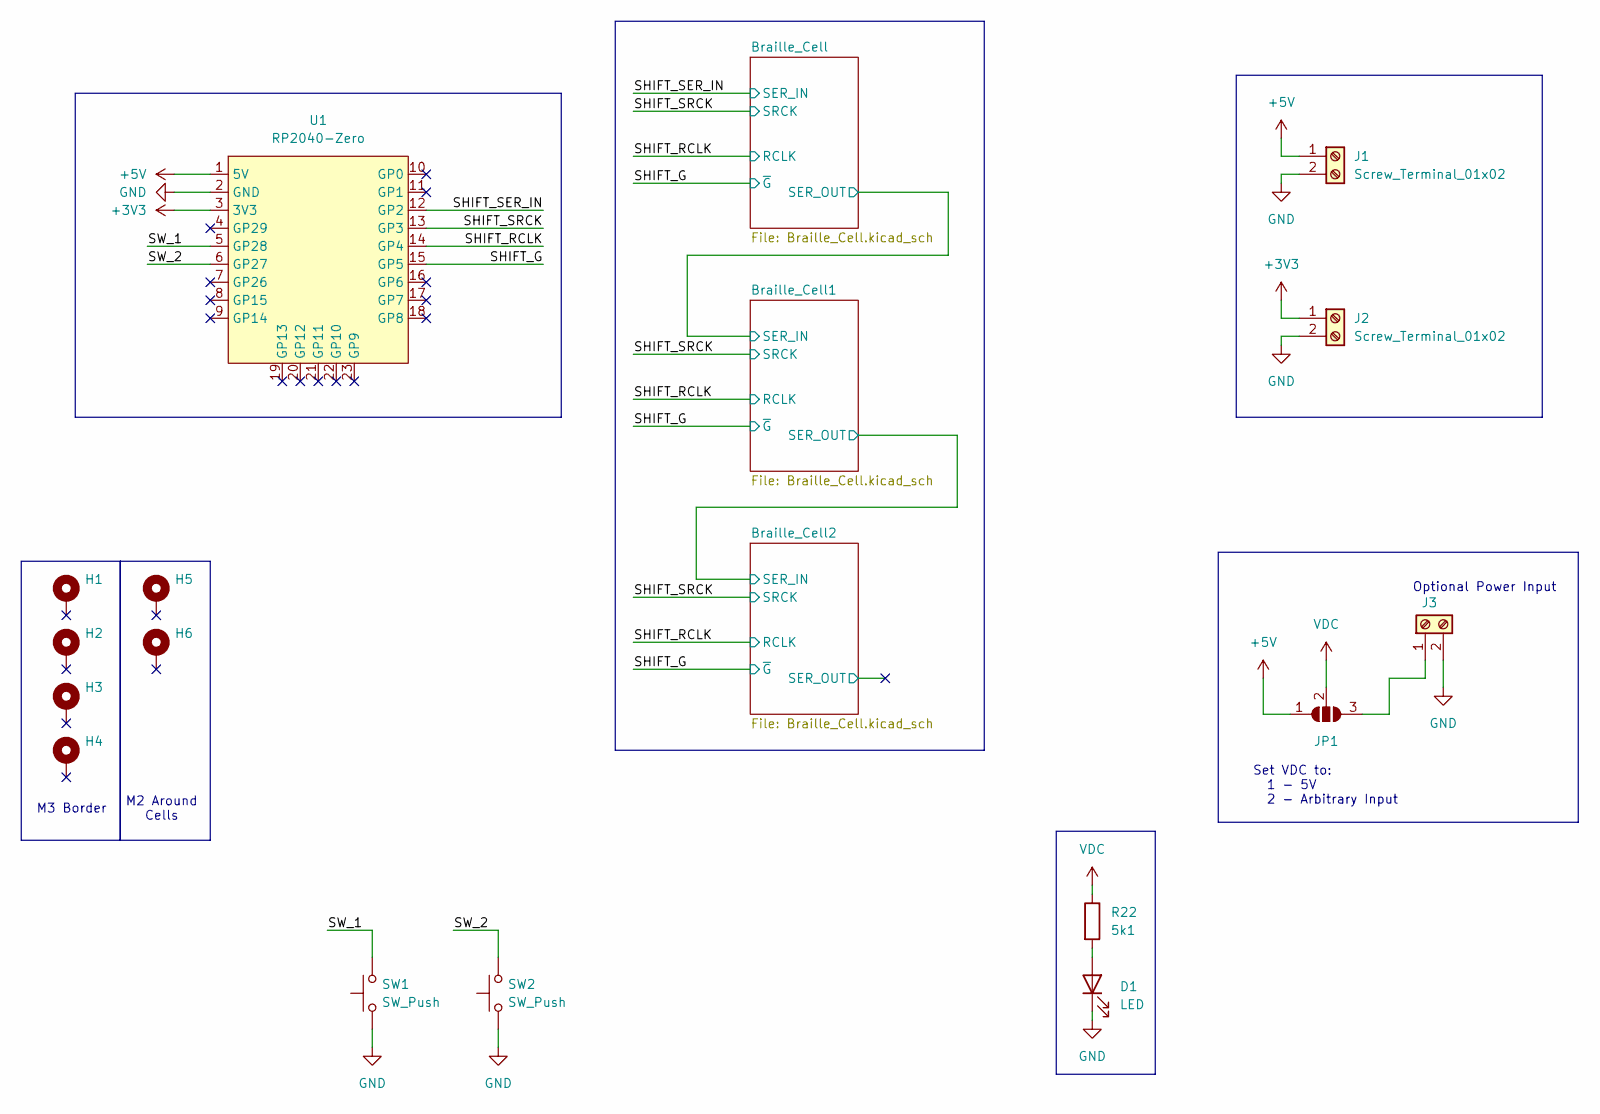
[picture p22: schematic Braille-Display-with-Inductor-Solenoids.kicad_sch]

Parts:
D1: LED; LED_1206_3216Metric_Pad1.42x1.75mm_HandSolder
H1, H2, H3, H4: MountingHole_Pad; MountingHole_3.2mm_M3_Pad
H5, H6: MountingHole_Pad; MountingHole_2.2mm_M2_Pad
J1, J2, J3: Screw_Terminal_01x02; TerminalBlock_bornier-2_P5.08mm
JP1: SolderJumper_3_Open; PinHeader_1x03_P2.54mm_Vertical
R22: 5k1; R_1206_3216Metric_Pad1.30x1.75mm_HandSolder
SW1, SW2: SW_Push; PushButtonSMD_2.93x3.9
U1: RP2040-Zero; RP2040 Zero

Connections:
+3V3: J2.1, U1.3 (3V3)
+5V: J1.1, JP1.1 (A), U1.1 (5V)
/SHIFT_G: U1.15 (GP5); also elsewhere on the board
/SHIFT_RCLK: U1.14 (GP4); also elsewhere on the board
/SHIFT_SER_IN: U1.12 (GP2); also elsewhere on the board
/SHIFT_SRCK: U1.13 (GP3); also elsewhere on the board
/SW_1: SW1.2, U1.5 (GP28)
/SW_2: SW2.2, U1.6 (GP27)
GND: D1.1 (K), J1.2, J2.2, J3.2, SW1.1, SW2.1, U1.2 (GND); also elsewhere on the board
unnamed: D1.2 (A), R22.2
unnamed: J3.1, JP1.3 (B)
VDC: JP1.2 (C), R22.1; also elsewhere on the board

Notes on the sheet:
M2 Around Cells
Optional Power Input
M3 Border
Set VDC to: 1 - 5V 2 - Arbitrary Input

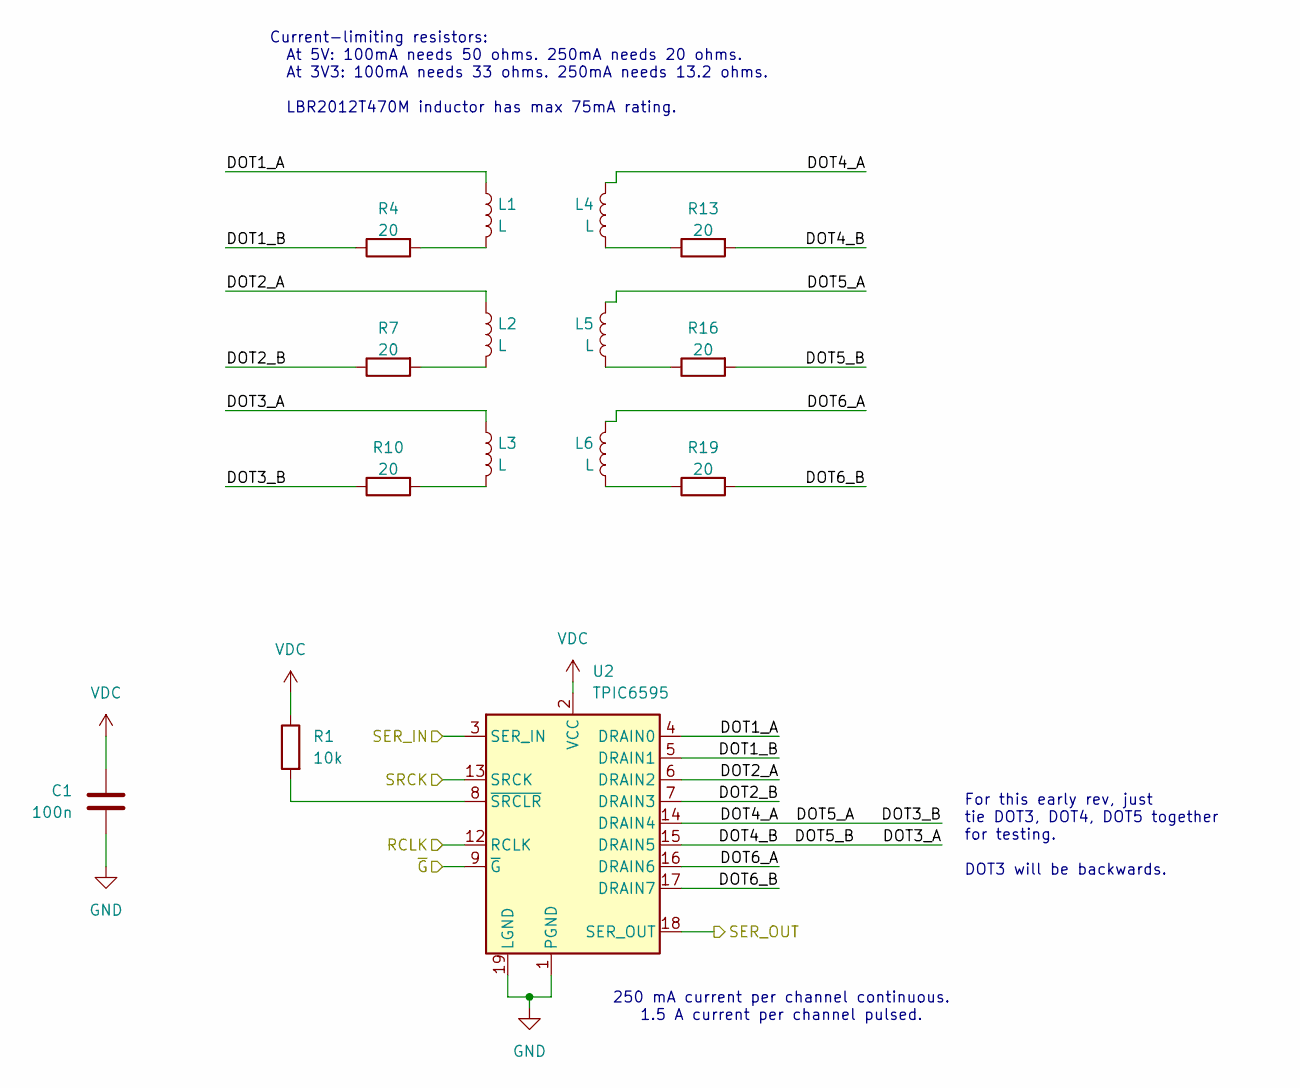
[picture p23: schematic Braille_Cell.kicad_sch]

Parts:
C1: 100n; C_0603_1608Metric
L1, L2, L3, L4, L5, L6: L; Inductor_0805_2012Metric_SMD_Vertical_Square
R1: 10k; C_0603_1608Metric_Pad1.08x0.95mm_HandSolder
R4, R7, R10, R13, R16, R19: 20; C_0603_1608Metric_Pad1.08x0.95mm_HandSolder
U2: TPIC6595; SOIC-20W_7.5x12.8mm_P1.27mm

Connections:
/Braille_Cell/DOT1_A: L1.1, U2.4 (DRAIN0)
/Braille_Cell/DOT1_B: R4.1, U2.5 (DRAIN1)
/Braille_Cell/DOT2_A: L2.1, U2.6 (DRAIN2)
/Braille_Cell/DOT2_B: R7.1, U2.7 (DRAIN3)
/Braille_Cell/DOT3_A: L3.1, R13.2, R16.2, U2.15 (DRAIN5)
/Braille_Cell/DOT3_B: L4.1, L5.1, R10.1, U2.14 (DRAIN4)
/Braille_Cell/DOT6_A: L6.1, U2.16 (DRAIN6)
/Braille_Cell/DOT6_B: R19.2, U2.17 (DRAIN7)
/Braille_Cell/SER_OUT: U2.18 (SER_OUT); also elsewhere on the board
/SHIFT_G: U2.9 (~G); also elsewhere on the board
/SHIFT_RCLK: U2.12 (RCLK); also elsewhere on the board
/SHIFT_SER_IN: U2.3 (SER_IN); also elsewhere on the board
/SHIFT_SRCK: U2.13 (SRCK); also elsewhere on the board
GND: C1.2, U2.1 (PGND), U2.10 (PGND), U2.11 (PGND), U2.19 (LGND), U2.20 (PGND); also elsewhere on the board
unnamed: L1.2, R4.2
unnamed: L2.2, R7.2
unnamed: L3.2, R10.2
unnamed: L4.2, R13.1
unnamed: L5.2, R16.1
unnamed: L6.2, R19.1
unnamed: R1.2, U2.8 (~SRCLR)
VDC: C1.1, R1.1, U2.2 (VCC); also elsewhere on the board

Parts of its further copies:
C2, C3: 100n; C_0603_1608Metric
L7, L8, L9, L10, L11, L12, L13, L14, L15, L16, L17, L18: L; Inductor_0805_2012Metric_SMD_Vertical_Square
R2, R3: 10k; C_0603_1608Metric_Pad1.08x0.95mm_HandSolder
R5, R6, R8, R9, R11, R12, R14, R15, R17, R18, R20, R21: 20; C_0603_1608Metric_Pad1.08x0.95mm_HandSolder
U3, U4: TPIC6595; SOIC-20W_7.5x12.8mm_P1.27mm

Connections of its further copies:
/Braille_Cell1/DOT1_A: L7.1, U3.4 (DRAIN0)
/Braille_Cell1/DOT1_B: R5.1, U3.5 (DRAIN1)
/Braille_Cell1/DOT2_A: L8.1, U3.6 (DRAIN2)
/Braille_Cell1/DOT2_B: R8.1, U3.7 (DRAIN3)
/Braille_Cell1/DOT3_A: L9.1, R14.2, R17.2, U3.15 (DRAIN5)
/Braille_Cell1/DOT3_B: L10.1, L11.1, R11.1, U3.14 (DRAIN4)
/Braille_Cell1/DOT6_A: L12.1, U3.16 (DRAIN6)
/Braille_Cell1/DOT6_B: R20.2, U3.17 (DRAIN7)
/Braille_Cell1/SER_OUT: U3.18 (SER_OUT), U4.3 (SER_IN)
/Braille_Cell2/DOT1_A: L13.1, U4.4 (DRAIN0)
/Braille_Cell2/DOT1_B: R6.1, U4.5 (DRAIN1)
/Braille_Cell2/DOT2_A: L14.1, U4.6 (DRAIN2)
/Braille_Cell2/DOT2_B: R9.1, U4.7 (DRAIN3)
/Braille_Cell2/DOT3_A: L15.1, R15.2, R18.2, U4.15 (DRAIN5)
/Braille_Cell2/DOT3_B: L16.1, L17.1, R12.1, U4.14 (DRAIN4)
/Braille_Cell2/DOT6_A: L18.1, U4.16 (DRAIN6)
/Braille_Cell2/DOT6_B: R21.2, U4.17 (DRAIN7)
/Braille_Cell2/SER_OUT: U4.18 (SER_OUT)
/Braille_Cell/SER_OUT: U3.3 (SER_IN); also elsewhere on the board
/SHIFT_G: U3.9 (~G), U4.9 (~G); also elsewhere on the board
/SHIFT_RCLK: U3.12 (RCLK), U4.12 (RCLK); also elsewhere on the board
/SHIFT_SRCK: U3.13 (SRCK), U4.13 (SRCK); also elsewhere on the board
GND: C2.2, C3.2, U3.1 (PGND), U3.10 (PGND), U3.11 (PGND), U3.19 (LGND), U3.20 (PGND), U4.1 (PGND), U4.10 (PGND), U4.11 (PGND), U4.19 (LGND), U4.20 (PGND); also elsewhere on the board
unnamed: L7.2, R5.2
unnamed: L8.2, R8.2
unnamed: L9.2, R11.2
unnamed: L10.2, R14.1
unnamed: L11.2, R17.1
unnamed: L12.2, R20.1
unnamed: L13.2, R6.2
unnamed: L14.2, R9.2
unnamed: L15.2, R12.2
unnamed: L16.2, R15.1
unnamed: L17.2, R18.1
unnamed: L18.2, R21.1
unnamed: R2.2, U3.8 (~SRCLR)
unnamed: R3.2, U4.8 (~SRCLR)
VDC: C2.1, C3.1, R2.1, R3.1, U3.2 (VCC), U4.2 (VCC); also elsewhere on the board

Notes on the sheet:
Current-limiting resistors: At 5V: 100mA needs 50 ohms. 250mA needs 20 ohms. At 3V3: 100mA needs 33 ohms. 250mA needs 13.2 ohms. LBR2012T470M inductor has max 75mA rating.
For this early rev, just tie DOT3, DOT4, DOT5 together for testing. DOT3 will be backwards.
250 mA current per channel continuous. 1.5 A current per channel pulsed.

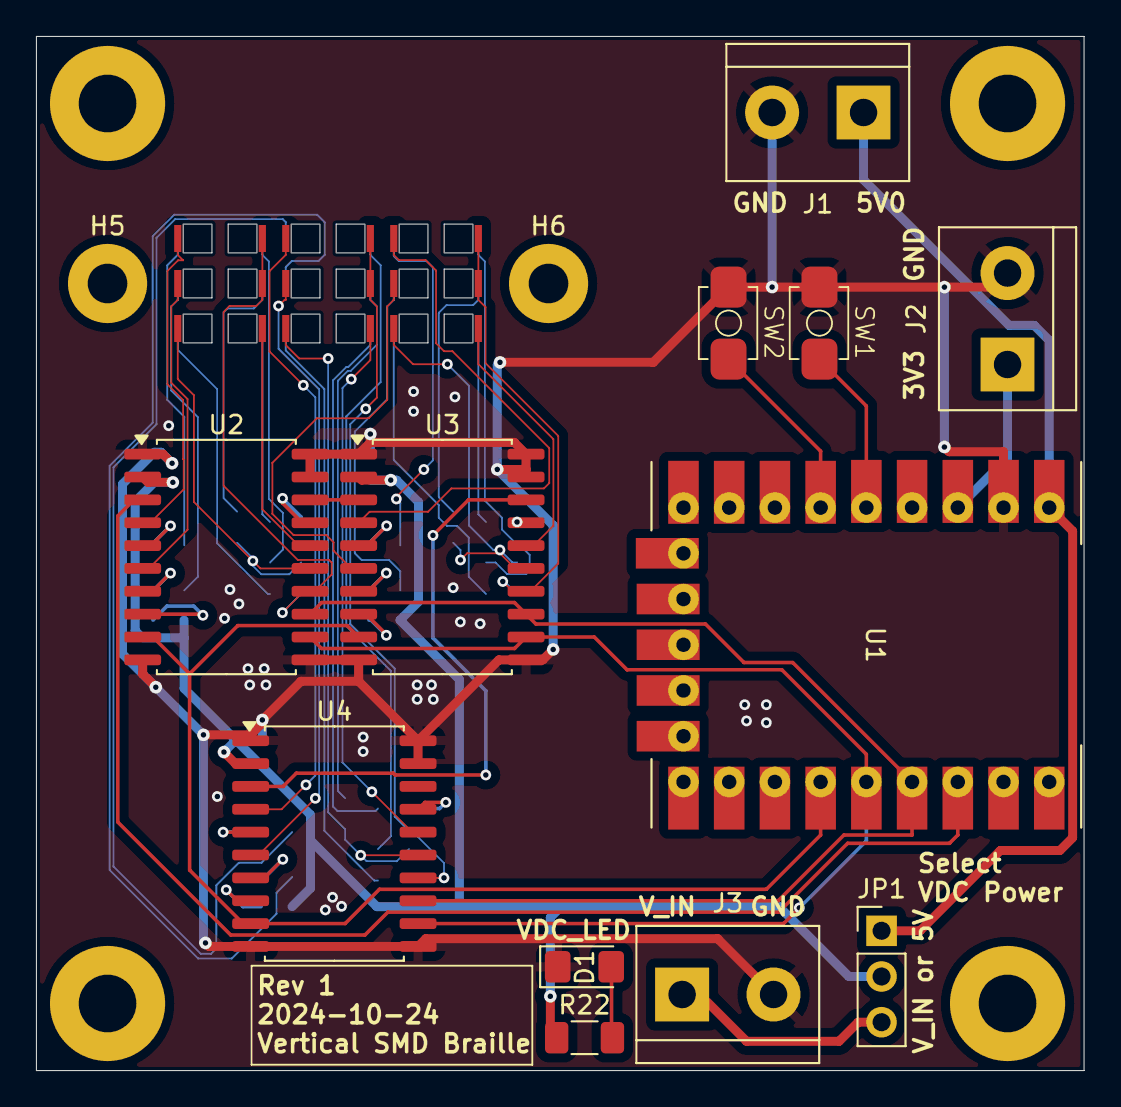
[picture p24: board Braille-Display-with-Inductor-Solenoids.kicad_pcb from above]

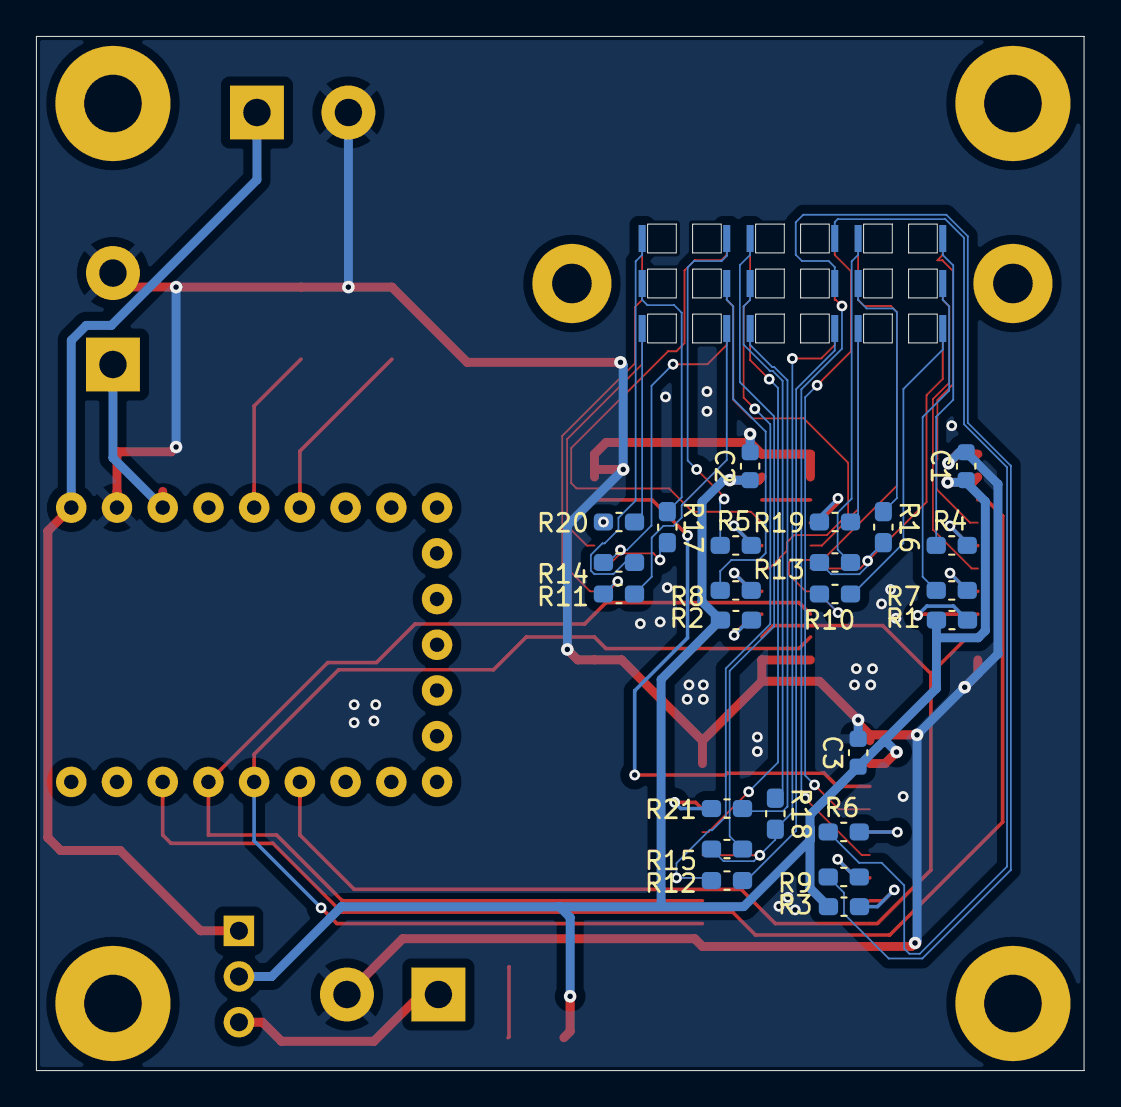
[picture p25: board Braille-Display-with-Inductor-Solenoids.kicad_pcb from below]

Board: 2 copper layers, 58.2 x 57.4 mm, 60 parts (24 on the bottom side), 59 nets.

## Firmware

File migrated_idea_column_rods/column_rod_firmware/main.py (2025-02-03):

from machine import ADC, Pin
import time

# Sleep a bit longer in init to ensure it gets set right.
SHIFT_REGISTER_INIT_SLEEP_MS = 100

# Sleep time between each bit shift.
SHIFT_REGISTER_SLEEP_US = 100

# Pin definitions for shift register control
PIN_SHIFT_SER_IN = Pin(2, Pin.OUT)  # GP2: Serial data input
PIN_SHIFT_SRCK = Pin(3, Pin.OUT)  # GP3: Shift register clock
PIN_SHIFT_N_SRCLR = Pin(4, Pin.OUT)  # GP4: Shift register clear
PIN_SHIFT_RCLK = Pin(5, Pin.OUT)  # GP5: Register clock (latch)
PIN_SHIFT_N_OE = Pin(6, Pin.OUT)  # GP6: Output enable

PIN_SW1 = Pin(28, Pin.IN, Pin.PULL_UP)
PIN_SW2 = Pin(27, Pin.IN, Pin.PULL_UP)
PIN_GP_LED_0 = Pin(7, Pin.OUT)
PIN_GP_LED_1 = Pin(8, Pin.OUT)

PIN_HALL_SELECT_0 = Pin(9, Pin.OUT)
PIN_HALL_SELECT_1 = Pin(10, Pin.OUT)
PIN_HALL_SELECT_2 = Pin(11, Pin.OUT)
PIN_HALL_SELECT_3 = Pin(12, Pin.OUT)
PINT_HALL_ADC = Pin(26, Pin.IN)

HALL_ADC = ADC(PINT_HALL_ADC)


def init_shift_register() -> None:
    """Initialize shift register pins to default states."""
    # Clear shift register.
    PIN_SHIFT_N_SRCLR.value(0)
    time.sleep_ms(SHIFT_REGISTER_INIT_SLEEP_MS)
    PIN_SHIFT_N_SRCLR.value(1)  # Active low, so set to normal (not clearing).
    time.sleep_ms(SHIFT_REGISTER_INIT_SLEEP_MS)

    PIN_SHIFT_N_OE.value(0)  # Active low, set low to enable outputs
    PIN_SHIFT_SRCK.value(0)  # Clock starts low
    PIN_SHIFT_RCLK.value(0)  # Latch starts low

    # Wait for initialization to complete
    time.sleep_ms(SHIFT_REGISTER_INIT_SLEEP_MS)

    # Clear all outputs.
    set_shift_registers([False] * 16)
    time.sleep_ms(SHIFT_REGISTER_INIT_SLEEP_MS)


def set_shift_registers(data: list[bool]) -> None:
    """
    Set the state of all shift registers based on input data.

    Args:
        data: list of 16 boolean values representing desired output states
             (6 registers x 8 bits per register)
    """
    if len(data) != 16:
        raise ValueError("Data must contain exactly 16 boolean values")

    # Shift out all 16 bits
    for bit in reversed(data):  # Shift MSB first
        # Set data bit.
        PIN_SHIFT_SER_IN.value(1 if bit else 0)
        time.sleep_us(SHIFT_REGISTER_SLEEP_US)

        # Clock in the bit.
        PIN_SHIFT_SRCK.value(1)
        time.sleep_us(SHIFT_REGISTER_SLEEP_US)
        PIN_SHIFT_SRCK.value(0)
        time.sleep_us(SHIFT_REGISTER_SLEEP_US)

    # Latch the data to outputs
    PIN_SHIFT_RCLK.value(1)
    time.sleep_us(SHIFT_REGISTER_SLEEP_US)
    PIN_SHIFT_RCLK.value(0)
    time.sleep_us(SHIFT_REGISTER_SLEEP_US)

def demo_each_corner_motor() -> None:
    """Spin each corner motor 1 sec in each direction."""

    DURATION_EACH_DIRECTION_MS = 200

    for motor_num in range(4):
        # Set the motor to spin in one direction.
        reg = [False] * 16
        reg[8 + motor_num * 2 + 0] = True
        reg[8 + motor_num * 2 + 1] = False
        set_shift_registers(reg)
        time.sleep_ms(DURATION_EACH_DIRECTION_MS)

        # Set the motor to spin in the other direction.
        reg = [False] * 16
        reg[8 + motor_num * 2 + 0] = False
        reg[8 + motor_num * 2 + 1] = True
        set_shift_registers(reg)
        time.sleep_ms(DURATION_EACH_DIRECTION_MS)

def init_hall_sensor() -> None:
    """Initialize the hall sensor pins to default states (select channel 15)."""
    PIN_HALL_SELECT_0.value(1)
    PIN_HALL_SELECT_1.value(1)
    PIN_HALL_SELECT_2.value(1)
    PIN_HALL_SELECT_3.value(1)


def read_hall_sensor_u16(sensor_num: int) -> int:
    """Read the hall sensor and return a 16-bit value."""
    # Select the correct hall sensor (using the mux).
    PIN_HALL_SELECT_0.value(sensor_num & 0b0001)
    PIN_HALL_SELECT_1.value(sensor_num & 0b0010)
    PIN_HALL_SELECT_2.value(sensor_num & 0b0100)
    PIN_HALL_SELECT_3.value(sensor_num & 0b1000)

    time.sleep_ms(10) # Wait for the sensor to settle.

    # Read the hall sensor.
    val = HALL_ADC.read_u16()

    # Reset the mux to default state.
    init_hall_sensor()

    return val

def demo_read_each_hall_sensor() -> None:
    """Read each hall sensor and print the value."""
    for i in range(16):
        val = read_hall_sensor_u16(i)
        print(f"Hall sensor {i}: {val:,}")

def demo_zeroing_corner_motor() -> None:
    """Try zeroing the top-left (U10 [corner 0] + U25 [hall 8]) corner motor."""
    reg_off = [False] * 16

    reg_cw = [False] * 16
    reg_cw[8 + 0] = True
    reg_cw[8 + 1] = False

    reg_ccw = [False] * 16
    reg_ccw[8 + 0] = False
    reg_ccw[8 + 1] = True

    for i in range(100):
        # Set the motor to spin in one direction.
        set_shift_registers(reg_cw)
        time.sleep_ms(10)
        set_shift_registers(reg_off)

        # Read the hall sensor.
        val = read_hall_sensor_u16(8)
        print(f"Hall sensor: {val:,}")

        time.sleep(1)


def main() -> None:
    print("Starting init.")
    init_shift_register()
    PIN_GP_LED_0.value(0)
    PIN_GP_LED_1.value(0)

    init_hall_sensor()
    print("Init complete.")

    print("Starting demo_zeroing_corner_motor()")
    demo_zeroing_corner_motor()
    print("Done demo_zeroing_corner_motor()")

    while 1:
        print("Starting demo_each_corner_motor()")
        demo_each_corner_motor()
        print("Done demo_each_corner_motor()")

        print("Starting demo_read_each_hall_sensor()")
        demo_read_each_hall_sensor()
        print("Done demo_read_each_hall_sensor()")

    # while 1:
    #     print("Starting rolling sphere demo.")
    #     braille_demo_try_to_roll_sphere()


while True:
    main()

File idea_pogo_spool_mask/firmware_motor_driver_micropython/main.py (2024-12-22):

import time

from machine import I2C, Pin
from neopixel import NeoPixel

PIN_ONBOARD_LED = 16
onboard_led_pin = Pin(PIN_ONBOARD_LED, Pin.OUT)


PIN_I2C_SDA = 26
PIN_I2C_SCL = 27
PIN_N_SLEEP_CELL_0 = 9
PIN_N_SLEEP_CELL_1 = 10
PIN_N_SLEEP_CELL_2 = 11  # U3/M3
PIN_N_SLEEP_CELL_3 = 12

PIN_N_FAULT_CELL_2 = 2  # U3/M3


# References:
# - https://www.ti.com/lit/ds/symlink/drv8847.pdf
# - https://www.tij.co.jp/lit/ug/tidued1a/tidued1a.pdf (start around Page 14/35)

# Notes:
# - Set nSLEEP to 1 to use the device (or pull it up).
# - Pull nFAULT LOW to release/sleep them. Pull nFAULT HIGH to talk to them.
# - Reprogram the addresses one-by-one using nFAULT.

# 0x60 = 96
DRV8847S_DEFAULT_I2C_ADDR = 0x60  # 7-bit address

i2c = I2C(1, scl=Pin(PIN_I2C_SCL), sda=Pin(PIN_I2C_SDA), freq=400000)
# pin_nfault_2 = Pin(PIN_N_FAULT_CELL_2, Pin.IN, Pin.PULL_UP)


REGISTER_ADDRESS_IC1_CONTROL = 0x01  # Control register address
REGISTER_ADDRESS_IC2_CONTROL = 0x02  # Control register address
REGISTER_ADDRESS_FAULT_STATUS_2 = 0x04  # Fault status register address

# HALF_STEP_SEQUENCE = [0x44, 0x4C, 0x0C, 0x2C, 0x24, 0x34, 0x14, 0x54]
HALF_STEP_SEQUENCE = [
    # 0b IN4 IN3 IN2 IN1
    0b1000,  # Sequence step 1
    0b1001,  # Sequence step 2
    0b0001,  # Sequence step 3
    0b0101,  # Sequence step 4
    0b0100,  # Sequence step 5
    0b0110,  # Sequence step 6
    0b0010,  # Sequence step 7
    0b1010,  # Sequence step 8
]

IC1_I2CBC_SELECT = 0b1  # Control via register instead of input pins.
IC1_MODE_4_INPUTS = 0b0  # 0b0=4-input interface.
IC1_TRQ_SETTING = 0b1  # 0b1=50% torque mode.

# Registers
# Table 7-15. I2C Registers
# | Addr | Acronym     | Register Name                | 7     | 6         | 5     | 4      | 3    | 2     | 1     | 0     | Access |
# |------|-------------|------------------------------|-------|-----------|-------|--------|------|-------|-------|-------|--------|
# | 0x00 | SLAVE_ADDR  | Slave Address                | RSVD  | SLAVE_ADDR|       |        |      |       |       |       | RW     |
# | 0x01 | IC1_CON     | IC1 Control                  | TRQ   | IN4       | IN3   | IN2    | IN1  | I2CBC | MODE  |       | RW     |
# | 0x02 | IC2_CON     | IC2 Control                  | CLRFLT| DISFLT    | RSVD  | DECAY  | OCPR | OLDOD | OLDFD | OLDBO | RW     |
# | 0x03 | SLR_STATUS1 | Slew Rate and Fault Status-1 | RSVD  | SLR       | RSVD  | nFAULT | OCP  | OLD   | TSDF  | UVLOF | RW     |
# | 0x04 | STATUS2     | Fault Status-2               | OLD4  | OLD3      | OLD2  | OLD1   | OCP4 | OCP3  | OCP2  | OCP1  | R      |
#
# IC1_CON register (main one)
# Default: Mode = 0b00 means 4-input interface.
# Must set the input pin control.
# Must set I2CBC=0b1 (control via register instead of input pins).
# Should set TRQ=0b1 (50% torque) to minimize overheat.
#
# IC2_CON register:
# Could explore DECAY: 0b0=25% fast (default) or 0b1=100% slow.
# Could explore SLR (slew rate): 0b0=150ns, 0b1=300ns


def write_register(address: int, register: int, value: int) -> None:
    """Write a single byte to a register on the DRV8847S."""
    print(f"write_register({address=}, {register=}, {value=}) ...")

    data = bytearray([register, value])
    i2c.writeto(address, data)


def read_from_register(address: int, register: int) -> int:
    """Read a single byte from a register on the DRV8847S."""
    i2c.writeto(address, bytearray([register]))
    data = i2c.readfrom(address, 1)
    val = data[0]
    print(
        f"read_from_register({address=}, {register=}) = {val} = 0x{val:x} = 0b{val:b} ..."
    )
    return val


def send_drive_command(
    i2c_addr: int, *, trq: int, step_value: int, i2cbc: int, mode: int
) -> None:
    """Send a drive command to the DRV8847S."""
    ic1_val = (trq << 7) | (step_value << 3) | (i2cbc << 2) | (mode << 1)
    write_register(i2c_addr, REGISTER_ADDRESS_IC1_CONTROL, ic1_val)


def drive_motor(
    step_period_sec: float,
    step_count: int,
    step_seq: list[int] = HALF_STEP_SEQUENCE,
    i2c_addr: int = DRV8847S_DEFAULT_I2C_ADDR,
) -> None:
    """Drive the motor."""
    # TODO: Support reverse direction.
    done_step_count = 0

    step_seq_run = step_seq[::-1] if step_count < 0 else step_seq
    abs_step_count = abs(step_count)

    while 1:
        for step_value in step_seq_run:
            # Enable TRQ = 50% torque mode (heat).
            send_drive_command(
                i2c_addr=i2c_addr,
                trq=IC1_TRQ_SETTING,
                step_value=step_value,
                i2cbc=IC1_I2CBC_SELECT,
                mode=IC1_MODE_4_INPUTS,
            )
            time.sleep(step_period_sec)
            done_step_count += 1

            if done_step_count >= abs_step_count:
                return


def disable_motor(i2c_addr: int = DRV8847S_DEFAULT_I2C_ADDR) -> None:
    """Disable the motor."""
    # Disable the motor.
    send_drive_command(
        i2c_addr=i2c_addr,
        trq=IC1_TRQ_SETTING,
        step_value=0,  # <- Set IN1=IN2 and IN3=IN4 to stop the motor.
        i2cbc=IC1_I2CBC_SELECT,
        mode=IC1_MODE_4_INPUTS,
    )


def i2c_scan():
    print("Scanning I2C buses")
    i2c_scan_result = i2c.scan()
    print(f"I2C scan result: {i2c_scan_result}")


def setup() -> None:
    i2c_scan()

    print("Setting nSLEEP to PULLED UP")
    pin_nsleep_2 = Pin(PIN_N_SLEEP_CELL_2, Pin.IN, Pin.PULL_UP)
    i2c_scan()

    time.sleep_ms(500)


def set_led_color(r: int, g: int, b: int) -> None:
    """Display a color on the LED.

    Values should be between 0 and 255.
    """
    np = NeoPixel(onboard_led_pin, 1)
    np[0] = (r, g, b)
    np.write()


def loop() -> None:
    print("Motor demo")

    # Might be 20 full steps per revolution.
    # 40 half steps per revolution (so 40 here).

    set_led_color(31, 31, 31)  # White.
    drive_motor(step_period_sec=0.02, step_count=-100)

    set_led_color(0, 31, 0)  # Green.
    drive_motor(step_period_sec=0.02, step_count=100)

    # Read the fault status register.
    fault_status_2 = read_from_register(
        DRV8847S_DEFAULT_I2C_ADDR, REGISTER_ADDRESS_FAULT_STATUS_2
    )
    if fault_status_2:
        print("Fault detected!")

    set_led_color(31, 0, 0)  # Red.
    disable_motor()
    time.sleep(2)


# Run `setup` and `loop`.
setup()
while True:
    loop()

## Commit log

2024-09-05 Create housing and snorkel cable tubes
2024-09-05 Add cable guides through the roof
2024-09-05 Tweak dimensions for test print
2024-09-09 Clean up housing channels out bottom
2024-09-12 Create motor base POC
2024-10-06 Add motor_base_1x part
2024-12-19 Add "pogo spool mask" idea (#2)
    [Braille-Pogo-Frame.kicad_pcb, Braille-Pogo-Frame.kicad_sch, Braille_Cell.kicad_sch, Mechanical_Holes.kicad_sch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]
2024-12-19 Add idea CAD - silicone sheet mold (#3)
2024-12-19 CAD - Solenoid Base Tubes and Coil Winding Adapter (#4)
2024-12-19 Create vertical motor layers demo (#5)
2024-12-19 Add nut/bolt grid base CAD (#6)
2024-12-19 Ball screw and housing CAD (#7)
2024-12-19 Add vertical and flat inductor PCBs (rev1) (#8)
    [Braille-Display-with-Inductor-Solenoids.kicad_pcb, Braille-Display-with-Inductor-Solenoids.kicad_sch, Braille_Cell.kicad_sch]
2024-12-22 Motor driver demo firmware - Add `disable_motor` function, reverse direction, better config
2024-12-23 Show dots in vertical motor layers demo
2024-12-23 Prep vertical motor layers housing CAD
2024-12-23 Add top plate CAD for vertical motor layers design
2024-12-24 Re-optimize vertical motor layers for no thin walls
2024-12-24 Add vertical motor layers variant for FDM
2024-12-27 Ball screw - Add print-in-place prototype
2024-12-27 Add additional turner lengths to ball screw concept
2024-12-29 Create generic column rod housing design (#12)
2024-12-29 Create octagon cam housing demo
2024-12-29 Add gear to octagon cam housing unit
2025-01-01 Create column rod enclosure
2025-01-02 Column rod cad: Add zeroing magnets, motor mate
2025-01-02 PCB - Column rods - start with big progress
    [Braille-Column-Rods-PCB.kicad_pcb, Braille-Column-Rods-PCB.kicad_sch, Braille_Cell_Column.kicad_sch, Corner_DC_Motor.kicad_sch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]
2025-01-06 Add explanation README for inductor magnets PCBs
2025-01-06 Create PCB and CAD for Type 4 Rev 1 rod cams (#13)
    * WIP: Rods PCB placement
    * WIP: Place the housing and motor X
    * WIP: Position everything
    * WIP: Update tight placement of DC motor
    * WIP: Layout and route the stepper driver
    * WIP: Motor layout is good
    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
    [Braille-Column-Rods-PCB.kicad_pcb, Braille-Column-Rods-PCB.kicad_sch, Braille_Cell_Column.kicad_sch, Corner_DC_Motor.kicad_sch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]
2025-01-09 Vertical motor layers: Add slice for one-layer-per-PCB assembly
2025-01-11 Move/rename folders to mark as migrated
    [Braille-Display-with-Inductor-Solenoids.kicad_pcb, Braille-Display-with-Inductor-Solenoids.kicad_sch, Braille_Cell.kicad_sch, horizontal_bar_holder.step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]
2025-02-03 Pin bad dependency
2025-06-30 Mark Column Rods design as migrated to separate repo
    [Braille-Column-Rods-PCB.kicad_pcb, Braille-Column-Rods-PCB.kicad_sch, Braille_Cell_Column.kicad_sch, Corner_DC_Motor.kicad_sch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]
